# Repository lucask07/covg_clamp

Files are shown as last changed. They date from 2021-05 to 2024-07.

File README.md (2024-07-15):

# COVG Clamp Board 



Schematic and layout for the COVG bath and guard clamps. This board sits near electrodes and includes a force output and a high-impedance feedback input to create a closed-loop clamp. Intention is to use the same design for the bath and guard clamps of a COVG amplifiers. The board supports digital programming of the current measurement gain and the feedback loop stability. Switching on the board allows for connect and disconnect of electrodes and injection (or measurements) of calibration signals onto an electrode.

### The PDF plot of the board schematic is [here](docs/bath_clamp.pdf) 
- 2D capture of the 3D model of the clamp board layout: 
<p align="center">
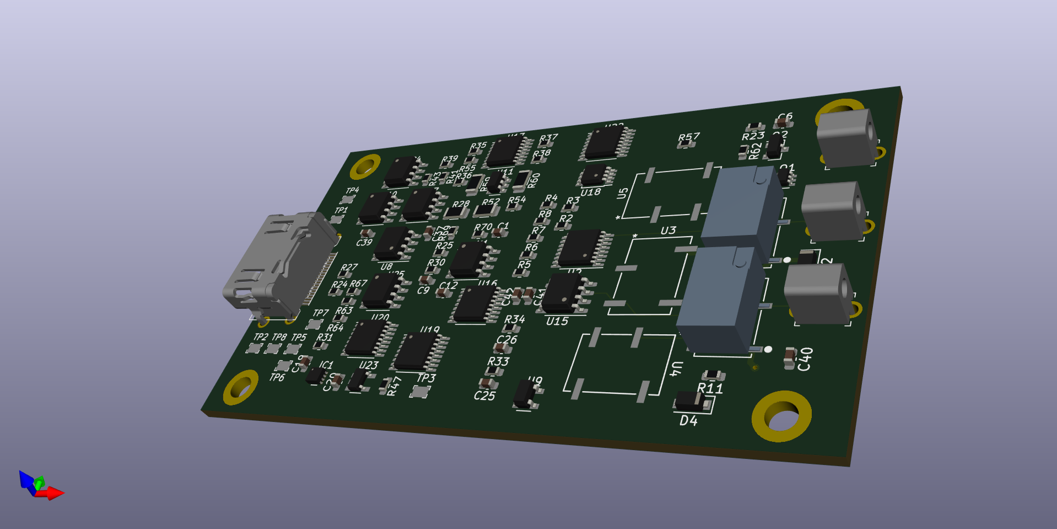
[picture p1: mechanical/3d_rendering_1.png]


## Acknowledgements 

If this work contributes to your research please cite:

I. Delgadillo Bonequi, A. Stroschein, and L. J. Koerner, “A field-programmable gate array (FPGA)-based data acquisition system for closed-loop experiments,” Review of Scientific Instruments, vol. 93, no. 11, p. 114712, Nov. 2022, [doi: 10.1063/5.0121898](http://doi.org/10.1063/5.0121898).

## HDMI: connection from DAQ to daughtercard 

The digital COVG project uses the concept of one main data acquition board connected to an FPGA. The main data acquisition board has multiple channels that extend to daughtercards. The connection to each daughtercard allows for low-latency control by connections to high-speed ADCs and DACs on the daq board. For COVG the daughtercards are the bath clamp; the guard clamp; the voltage clamp and I force; and the V1/V2. The connectivity to the daughtercard is generalized and will be the same for each. 

An HDMI-A cable is used for input and output signals that connects the bath clamp daughtercard to the DAQ board. The HDMI cable carries:

- **power**: +5V, +15V, -15V
- **GND** 
- **Analog outputs** (to ADCs): 
	- OUT\_P, OUT\_N differential pair (x1) to 5 MSPS ADC 
	- single-ended out AMP\_OUT, CAL\_ADC both to individual channel of 1 MSPS ADC (ADS8686) 
- **Analog reference**: VCM: buffered ADC common-mode voltage (nominal 2.5 V)
- **Digital inputs** (from DACs): 
	- CMD: (command signal) from 1 us settling time DAC (attenuated by x10 at board)
	- CC: (capacitive compensation) from 1 us settling time DAC. AC coupled. 
	- CAL_DAC: from 5 us settling time DAC (DAC8050). Either voltage source or current source (Howland current pump), programmable on DAQ board
- **Digital control** (I2C): SDA, SCL (@ 3.3 V levels). Pull-ups are on DAQ board not on the daughtercards! The daughtercards use a TCA9555 I/O expander to generate many control signals from the I2C interface. 
- **Utiility** grab-bag connected to test-point. Jumper on DAQ board to set to analog in, analog out or digital I/O.

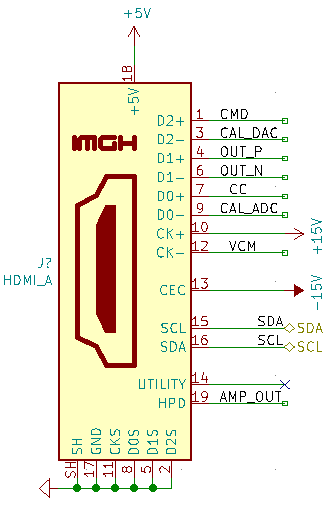
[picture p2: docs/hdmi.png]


| Pin | HDMI name    | Generic Daughtercard     | Bath clamp | Notes  |
|-----|--------------|--------------|------------|---------------------------------------------------------------------------|
| 1   | Data2+       | fastDAC1     | CMD        | ~1 us settling time                      |
| 2   | Data2 shield | Gnd          | Gnd        |                                                                           |
| 3   | Data2-       | Analog/GPIO1 | CAL_DAC    | Analog input signal from DAC8050, 16 bit, 5us settle, 5 V supply                                                                         |
| 4   | Data1+       | fastADC+     | IM_P       | to AD7960/AD7961. Differential low-pass filter on DAQ board                                                                          |
| 5   | Data1 shield | Gnd          | Gnd        |                                                                           |
| 6   | Data1-       | fastADC-     | IM_N       | to AD7960/AD7961. Differential low-pass filter on DAQ board                                                                          |
| 7   | Data0+       | fastDAC2     | CC         | ~1 us settling time                                                                          |
| 8   | Data0 shield | Gnd          | Gnd        |                                                                           |
| 9   | Data0-       | Analog/GPIO2 | CAL_ADC    | to ADS8686 1 MSPS, programmable PGA for range up to +/-10V                                                           |
| 10  | Clock+       | 15V          | 15V        | From a linear regulator on the DAQ board, 75 mA max per channel                                                                         |
| 11  | Clock shield | Gnd          | Gnd        |                                                                           |
| 12  | Clock-       | VCM          | VCM        | buffered on DAQ board, nominal 2.5 V                                                                          |
| 13  | CEC          | -15V         | -15V       | From a linear regulator on the DAQ board, 75 mA max per channel                             |
| 14  | Reserved     | open         | open       | Resistor jumper on DAQ board sets as analog in, analog out, or digital I/O (@ 3.3 V levels). Default stuffing option is to connect to the general purpose ADC (ADS8686). |
| 15  | SCL          | SCL          | SCL        | I2C clock. Pull-up on main DAQ board, 3.3 V levels                |
| 16  | SDA          | SDA          | SDA        | I2C data. Pull-up on main DAQ board, 3.3 V levels                 |
| 17  | Gnd          | Gnd          | Gnd        |                                                                           |
| 18  | 5V           | 5V           | 5V         | Power input from linear regulator, 200 mA max per channel (target)  |
| 19  | HPD          | Analog/GPIO3 | AMP_OUT    | output to ADS8686 1 MSPS, programmable PGA                        |

## Electrode Configurations and Modes 

### Electrodes

The electrode connections are [tip jack miniature PCB mount connectors](https://www.digikey.com/en/products/detail/cinch-connectivity-solutions-johnson/105-1103-001/241122?s=N4IgTCBcDaIIwAYCsBaOiDMKELiAugL5A) for 0.08" diameter pin connections. 

- J1 corresponds to Dagan P2 - force
- J2 corresponds to Dagan P1 - sense
- J3 corresponds to Dagan CC - capacitive compensation 

### Modes 
**Electrode diagnositcs / calibration / system ID** 

Five relays are used to:

1. Disconnect the electrodes from the active electronics (relay K2, K1). Digital control signals: *P1\_E\_CTRL*, *P2\_E\_CTRL*
2. Switch between active and passive clamp (U3). Digital control signals: *P\_CLAMP\_CTRL*
3. Connect calibration signals (ADC or DAC) to the electrodes (U4, U5). Digital control signals: *P1\_CAL\_CTRL*, *P2\_CAL\_CTRL*
A logical high digital control signal closes the Ux relays. A logical high swicthes the Kx relays so that the electronics and electrodes are disconnected. 

**Calibration** 
When "calibrating" the electrode that is driven by a DAC signal or output along the ADC signal CAL\_ADC is programmable. This output multiplexing is set by DAC\_SEL[1..4] and ADC\_SEL[1..4]. Via DAC\_SEL[1..4] an electrode can be connected to CAL\_DAC or GND. The ADC\_SEL[1..4] controls the signal that is connected to CAL\_ADC pin the options are (CAL\_SIG1, CAL\_SIG2, INAMP\_OUT, CC).   

**Clamping**

- _Voltage clamp_: U1 drives the command voltage (CMD) to electrode P2. Nominal voltage clamp mode will have all 5 relays in nominal position (with 0 coil current).  When in voltage clamp mode the current to P2 (as measured by the voltage across nets RF\_1 and P2) is output by the different ADC driver for 5 MSPS digitization. The settings for U22 (TMUX6136) are S1 = 1 for  the inamp output to be buffered out to the 5 MSPS ADC; and S2 = 1 so that the instrumentation amplifier amplifies the voltage difference: (P2 - RF_1). The voltage feedback in voltage clamp mode can be enabled/disabled by the I/O expander siganl *FDBK* (*FDBK*=0 is disabled). 

- _Current clamp_: The board has a Howland current source that can be used to set the current to P2 based upon the CMD signal (requires A2=A1=A0=0). The output current can range from +/-0.26 nA (with a 1.22 mV CMD) to +/-2.1 uA (with a 10 V CMD signal). To enable the current clamp either float or drive high the signal EN\_IPUMP. To shutoff the amplifier set EN\_IPUMP to a logical 0. When in current clamp mode the intent is that the 5 MSPS ADC measurement is of P1 (i.e. set current and measure voltage). This is accomplished by these settings for U22 (TMUX6136): S1 = 0 so that the P2 buffer output voltage is sent to the 5 MSPS ADC; and S2 = 0 so that the instrumentation amplifier amplifies P2 - 0 (RF_1 voltage will not make sense in this mode). In this mode the instrumentation amplifier output can buffer out the CAL\_OUT line to a 1 MSPS ADC channel. 

### Adjustments for clamp stability 
The P2 signal is amplified and buffered before being fedback to the main clamp amplifier (U15 within feedback\_buffer). The stability of this loop varies depending upon the load presented by the cell under test, electrode electrical characteristics, and parasitic capacitive coupling between electrodes. The stability of this feedback loop can be adjusted by modification of the feedback buffer gain and by changing the capacitance of a lead compensator at the summing junction of the main amplifier (inverting terminal). 

**Feedback buffer gain**

The feedback buffer is a non-inverting structure with an adjustable gain set by I/O expander bits RF[1..4]. The feedback resistor values are 3.01k, 12.1k, 30.1k, and 60.4k. The resistor from the inverting terminal to "ground" is 3.01k creating gains of 

- x2 = 1+3.01k/3.01k 
- x5 
- x11
- x21 

**Feedback buffer offset**

The feedback buffer has offset adjustment. This is generated by a 10-bit I2C interface DAC, IC1 (DAC53401), followed by a unipolar to bipolar amplifier (U23). The output of the bipolar converter ranges between +/-1 V (resolution of 1.9 mV / bit). OUT = VDAC*1.666-1. 

(simulation: non\_inverting\_rpot\_bw.asc)

**Compensation adjustment**

Adjustments of the closed-loop stability are achieved using four approaches. 

- The primary approach is a lead compensator formed by R30 in parallel with the capacitors in the compensation switching sheet. This method is presented in "Voltage Clamping of Excitable Membranes" by Bezanilla, Vergara, and Taylor. The compensation capacitors (47 pF, 200 pF, 1 nF, 4.7 nF) are selectable using the the TMUX6111 I/O expander bits CCOMP[1..4].
- A second approach is adjusting the gain of the feedback buffer (see above). 
- A third approach is a stabilizing feedback network of R in series with C; simulations have shown little beneift of this network. Also, beware that the C forms a pole with the current resolving resistor (R\_F) which can be very low frequency. The footprints for these components are included by not populated. This is also presented in Bezanilla, et al.
- The fourth potential approach is an input lead-lag compensator formed by R69 and C37 (unpopulated). See [TI App Note AN-1604](https://www.ti.com/lit/an/snoa486b/snoa486b.pdf?ts=1623954308102&ref_url=https%253A%252F%252Fwww.google.com%252F)

### Adjustments for current measurement

The current measurement gain (historically reported in units of mV/nA) is determined by three separate "stages".

**Resolving inline resistor**: is set by component U2 which is an analog switch (ADG1208) that determines the resistance across which the clamp current is measured. 

| Ref. Des. | Value    | mV/nA            | A2,A1,A0 | Closed Switch   | 
|-----|--------------|--------------|------------|------------|
| none -> Iclamp| n/a | n/a | 0,0,0 | Sw1 |
| R2   | 10 kOhm       |  0.01       | 0,0,1 | Sw2      | 
| R3   | 33.2 kOhm       |  0.033       | 0,1,0 | Sw3      | 
| R4   | 100k Ohm       |  0.1       | 0,1,1 | Sw4      | 
| R5   | 332 kOhm       |  0.332       | 1,0,0 | Sw4      | 
| R6   | 1 MOhm       |  1       | 1,0,1 | Sw5      | 
| R7   | 3.32 MOhm       |  3.32       | 1,1,0 | Sw6      | 
| R8   | 10 MOhm       |  10       | 1,1,1 | Sw7      | 

**Instrumentation Amplifier gain**  

There is a second stage that allows for additional gain on the analog output signal before ADC conversion. The gain of the instrumentation amplifier (AD8421) within the adc\_driver block gain is adjusted with bits G[1..3].
The gain options as controled by U17 (DG412 switch) are: 

- G = 1, G1=G2=G3=0, all switches open 
- G = 1.99, G1 = 1, others = 0 
- G = 4.98, G2 = 1, others = 0
- G = 10.00, G3 = 1, others = 0 
- G = 50, This setting is currently not programmable but set by resistors. 
- Other gains are available by combining the gain settings resistors in parallel. 

For the instrumentation amplifier Gain = 1 + 9.9 kOhm/RG 

**Output ADC driver gain**

The ADC output driver implements a gain of around 1/3 (0.308 = 499 Ohms/(1500 + 120) Ohms) to scale the maximum output of the instrumenation amplifer (+/-13.5 V) to the range of the AD796x ADC (+/-4.096 V).

**Total gain** 

(without the G = 50 option of the instrumentation amplifier) the available gain ranges are:

- min: 0.00308 mV/nA 
- max: 30.8 mV/nA. 

Since the ADC covers a range of +/-4.096 V at 16-bit resolution for step-sizes of:

- min-gain: 0.0246 LSB/nA  (40.6 nA/LSB)
- max-gain: 246.4 LSB/nA  (4.06 pA/LSB)

The amplifier noise simulates to be (very roughly) 1 nA RMS, such that ADC quantization noise will not limit amplifier performance when high-gain settings are used.

## I2C Address Table
| Component | Description | I2C address | I2C mode | 
| --------- | -------- | ------------| ------------|
| U12    | I/O expander 0: TCA9555       | 0x26 = 'b010\_0110 | Standard, Fast |
| U13    | I/O expander 1: TCA9555        | 0x20 = 'b010\_0000 | Standard, Fast |
| U6   | Unique ID EEPROM: 24AA025UID    | 0x50 = 'b101\_0000 | Standard, Fast |
| IC1   | Offset adj. DAC: DAC53401  | 0x48 = 'b100\_1000 | Standard, Fast, Fast+ |

## Current Draw

+/-15 V  (or from the +7V and -2.5 V supplies derived from +/-15 V) 

| Component | Quantity | Current [mA]| Total [mA] |
| --------- | -------- | ------------| ---------- |
| OPA828    | 2        | 5.5 | 11 |
| OPA2156   | 2 (dual) | 4.4 | 8.8 |
| OPA991S   | 1        | 0.56 | 0.56 |
| ADG1208   | 1        | 0.0001 | 0 |
| ADG1208   | 1        | 0.0001 | 0 |
| AD8421    | 1        | 2.3    | 2.3 |
| ADA4932 (ADC driver)  | 1        | 9.6    |     |
| or LMP8350 (ADC driver) |         | 15 (HP mode) | 15 |
|           |          |        | Totals (w/ LMP) |
|           |          |        |    37.66 |

## For Board and FPGA Designers

## KiCAD Setup (libraries)
Before opening the project complete these steps to setup your parts libraries. 

* On the main Kicad Menu bar click 'Preferences' -> 'Configure Paths'. 
* Then within the 'Configure Paths' window create an Environmental Variable with the 'Name' MYLIBRARY.
* Set the 'Path' to be where you will store the Digikey libraries and the COVG custom library. For example (this is on a MAC) '/Users/lucas/Documents/kicad/libraries'.

Now *git clone* (effectively download) the digikey and COVG libraries. 

* The Digikey library is at [https://github.com/Digi-Key/digikey-kicad-library](https://github.com/Digi-Key/digikey-kicad-library)
	* Use the terminal command: `git clone https://github.com/Digi-Key/digikey-kicad-library.git ` 

* The custom COVG library is at [https://github.com/lucask07/covg-kicad-lib](https://github.com/lucask07/covg-kicad-lib)
	* Use the terminal command: `git clone https://github.com/lucask07/covg-kicad-lib.git `
	* This is a private repository so will require you to request access to the repository from Lucas. 

Symbols and footprints custom to this design (and the COVG project in general) are housed in the [covg-kicad-lib repository](https://github.com/lucask07/covg-kicad-lib). This library should be a project specific library in your KiCAD *Symbol Library Management* and *Footprint Library Management*. 

* Another library in use is the [agg library](https://github.com/adamgreig/agg-kicad)

### LMP8350 ADC Driver 

Initial designs used the ADA4932-1 differential ADC driver to drive the AD7961 on the DAQ board. However, as part of the "chip shortage of 2021" there parts were hard to find in spring of 2021. An alternative part (and possibly better option) used for this board is the [LMP8350](https://rocelec.widen.net/view/pdf/d6pm6sbaz5/lmp8350.pdf?t.download=true&u=5oefqw).

## BOM (bill of materials)

The BOM is available [here](bom/bath_clamp_v1_bom.xlsx)

Two command-line tools are useful for finding and ordering the parts for the board. 

[kifield](https://xess.com/KiField/docs/_build/singlehtml/index.html): extracts all fields from components on the schematic into a spreadsheet and also allows for "injecting" updates in the spreadsheet into the schematic.

Example to extract parts:
```kifield -x covg_daq_v2.sch --recurse -i covg_daq_v2_parts.csv```

**Don't import parts from the CSV into the board! This seems to incorrectly update some components!!**:
``` kifield -x covg_daq_v2_parts.csv --recurse -i covg_daq_v2.sch ```

[kicost](https://github.com/xesscorp/KiCost) which scrapes availability and prices from various distributors and creates a spreadsheet of component cost. 

## Changelog (v1 ---> v2)
List on NB#1 pg 76.

1. Add an 'Alternate Manf#' field to all ICs (where possible). The alternative part must be pin compatible. If available add an 'Alternate2 Manf#'. If the alternative part requires a footprint change the field is 'Alternate Manf# (footprint diff)'.
2. Use +/-15 V op-amp to buffer 3.3 V into amplifier. Eliminates problem of the 3.3 V net rising since the regulator cannot sink current. 
3. Switch to a DAC with leads to improve solderability. Part chosen was the DAC101C081CIMK/NOPB.
4. Correct ADG1208 Manf# to ADG1208YRUZ so that the package matches the footprint (16-TSSOP).  
5. Switch LM337 negative regulator to MIC5270YM5-TR (alternate MIC5270-4.1YM5-TR, fixed -4.1 V).  Another option considered was the TPS7A3401DGNT. 
6. Change resistor values in adjustable regulators for lower negative voltage. The negative regulator is designed for either an adjustable version or a fixed voltage. The resistor values are 487 Ohm and 240 Ohm for -3.635 Volts. 
7. Need alternative to the AD8421 instrumentation amplifier in 8-MSOP. Locating an 8-MSOP instrumentation amplifier was challenging. Switched to an 8-SOIC footprint. 
8. The SMT SPDT relay 1462042-8 was not avaliable. The through hole version is available 1462042-7. Added new footprint to covg-library named Relay_SPDT_TE_1462042-7.
9. Need alternative to the TMUX6136 (or switch to a 4x SPST + 2 channel inverter). The findchips risk for the TMUX6136 was low so kept this part but added 0 Ohm resistors that can be populated for a default MUX configuration.
10. Mini banana  NOT YET DONE!
11. More ground test points  NOT YET DONE!
12. Fixed swap of SCL and SDA (correct by changing routing at the connector to keep other routing correct) NOT YET DONE!
13. The TCA9555DBR (IO expander) has another Manf# for the same part as TCA9555DBT. The PCA9555 is an older part that is also compatible with the TCA9555. 
14. The microchip 3.3 V regulator is not available (MCP1804T-3302I/OT). 

Use the Value field to indiciate DNI (do not install) but keep the MANF# up to date. 

## Funding 
Research reported in this publication was supported by the National Institute Of Neurological Disorders And Stroke of the National Institutes of Health under Award Number R15NS116907. The content is solely the responsibility of the authors and does not necessarily represent the official views of the National Institutes of Health.

<!---
## Block diagram - To Be Completed! 
drawio (also named add.diagrams.net) is used to create block diagrams by integrating drawio with the GitHub repository. 

![Test block diagram](docs/test_github.svg)

--->

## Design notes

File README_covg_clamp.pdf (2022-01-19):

Schematic and layout for the COVG bath and guard clamps. This board sets near electrodes and includes a force output and a high-impedance feedback input to create a closed-loop clamp. Intention is to use the same design for the bath and guard clamps of a COVG amplifiers. The board supports digital programming of the current measurement gain and the feedback loop stability. Switching on the board allows for connect and disconnect of electrodes and injection (or measurements) of calibration signals onto an electrode.

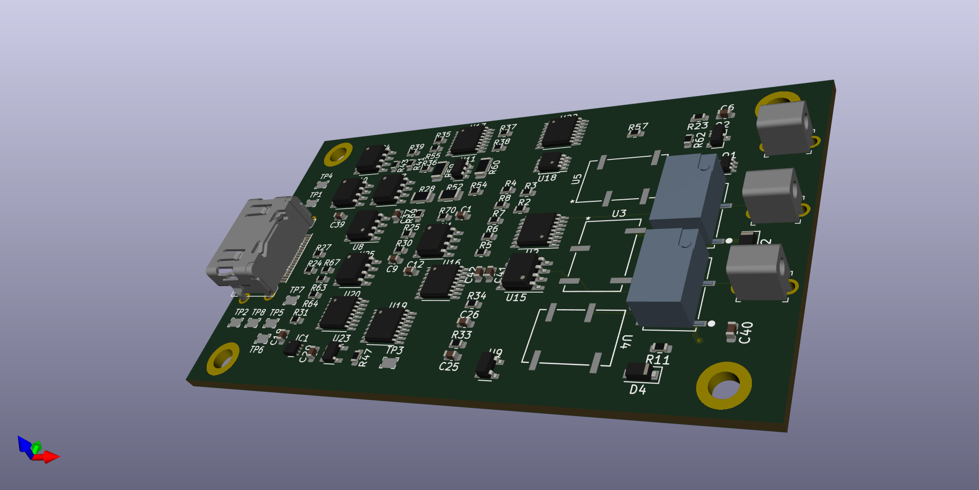
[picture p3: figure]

2D capture of the 3D model of the clamp board layout:

The digital COVG project uses the concept of one main data acquition board connected to an FPGA. The main data acquisition board has multiple channels that extend to daughtercards. The connection to each daughtercard allows for low-latency control by connections to high-speed ADCs and DACs on the daq board. For COVG the daughtercards are the bath clamp; the guard clamp; the voltage clamp and I force; and the V1/V2. The connectivity to the daughtercard is generalized and will be the same for each.

An HDMI-A cable is used for input and output signals that connects the bath clamp daughtercard to the DAQ board. The HDMI cable carries:

power: +5V, +15V, -15V
GND
Analog outputs (to ADCs):

OUT_P, OUT_N differential pair (x1) to 5 MSPS ADC

# COVG Clamp Board

## The PDF plot of the board schematic is here

# HDMI: connection from DAQ to daughtercard

single-ended out AMP_OUT, CAL_ADC both to individual channel of 1 MSPS ADC (ADS8686)

Analog reference: VCM: buffered ADC common-mode voltage (nominal 2.5 V)
Digital inputs (from DACs):

CMD: (command signal) from 1 us settling time DAC (attenuated by x10 at board)
CC: (capacitive compensation) from 1 us settling time DAC. AC coupled.
CAL_DAC: from 5 us settling time DAC (DAC8050). Either voltage source or current source (Howland current pump), programmable on DAQ board

Digital control (I2C): SDA, SCL (@ 3.3 V levels). Pull-ups are on DAQ board not on the daughtercards! The daughtercards use a TCA9555 I/O expander to generate many control signals from the I2C interface. Utiility grab-bag connected to test-point. Jumper on DAQ board to set to analog in, analog out or digital I/O.

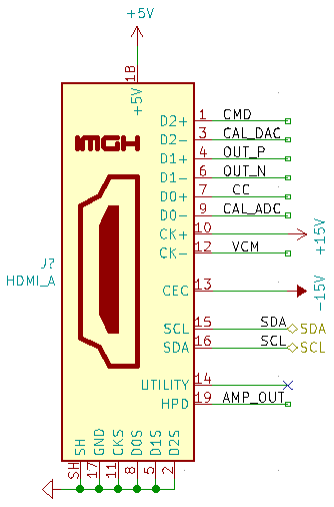
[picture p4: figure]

Pin | HDMI | Generic | Bath | Notes

| name | Daughtercard | clamp
1 | Data2+ | fastDAC1 | CMD | ~1 us settling time
2 | Data2 shield | Gnd | Gnd
3 | Data2- | Analog/GPIO1 | CAL_DAC | Analog input signal from DAC8050, 16 bit, 5us settle, 5 V supply
4 | Data1+ | fastADC+ | IM_P | to AD7960/AD7961. Differential low-pass filter on DAQ board
5 | Data1 shield | Gnd | Gnd
6 | Data1- | fastADC- | IM_N | to AD7960/AD7961. Differential low-pass filter on DAQ board
7 | Data0+ | fastDAC2 | CC | ~1 us settling time
8 | Data0 shield | Gnd | Gnd
9 | Data0- | Analog/GPIO2 | CAL_ADC | to ADS8686 1 MSPS, programmable PGA for range up to +/-10V
10 | Clock+ | 15V | 15V | From a linear regulator on the DAQ board, 75 mA max per channel
11 | Clock shield | Gnd | Gnd
12 | Clock- | VCM | VCM | buffered on DAQ board, nominal 2.5 V
13 | CEC | -15V | -15V | From a linear regulator on the DAQ board, 75 mA max per channel
14 | Reserved | open | open | Resistor jumper on DAQ board sets as analog in, analog out, or digital I/O (@ 3.3 V levels). Default stuffing option is to connect to the general purpose ADC (ADS8686).
15 | SCL | SCL | SCL | I2C clock. Pull-up on main DAQ board, 3.3 V levels

16 | SDA | SDA | SDA | I2C data. Pull-up on main DAQ board, 3.3 V levels
17 | Gnd | Gnd | Gnd
18 | 5V | 5V | 5V | Power input from linear regulator, 200 mA max per channel (target)
19 | HPD | Analog/GPIO3 | AMP_OUT | output to ADS8686 1 MSPS, programmable PGA

The electrode connections are tip jack miniature PCB mount connectors (https://www.digikey.com/en/products/detail/cinch-connectivity-solutions-johnson/105-1103-001/241122?s=N4IgTCBcDaIIwAYCsBaOiDMKELiAugL5A) for 0.08" diameter pin connections.

J1 corresponds to Dagan P2 - force
J2 corresponds to Dagan P1 - sense
J3 corresponds to Dagan CC - capacitive compensation

Electrode diagnositcs / calibration / system ID

Five relays are used to:

1. Disconnect the electrodes from the active electronics (relay K2, K1). Digital control signals: P1_E_CTRL, P2_E_CTRL
2. Switch between active and passive clamp (U3). Digital control signals: P_CLAMP_CTRL
3. Connect calibration signals (ADC or DAC) to the electrodes (U4, U5). Digital control signals: P1_CAL_CTRL, P2_CAL_CTRL A logical high digital control signal closes the Ux relays. A logical high swicthes the Kx relays so that the electronics and electrodes are disconnected.

Calibration When "calibrating" the electrode that is driven by a DAC signal or output along the ADC signal CAL_ADC is programmable. This output multiplexing is set by DAC_SEL[1..4] and ADC_SEL[1..4]. Via DAC_SEL[1..4] an electrode can be connected to CAL_DAC or GND. The ADC_SEL[1..4] controls the signal that is connected to CAL_ADC pin the options are (CAL_SIG1, CAL_SIG2, INAMP_OUT, CC).

Clamping

Voltage clamp: U1 drives the command voltage (CMD) to electrode P2. Nominal voltage clamp mode will have all 5 relays in nominal position (with 0 coil current). When in voltage clamp mode the current to P2

# Electrode Configurations and Modes

## Electrodes

## Modes

(as measured by the voltage across nets RF_1 and P2) is output by the different ADC driver for 5 MSPS digitization. The settings for U22 (TMUX6136) are S1 = 1 for the inamp output to be buffered out to the 5 MSPS ADC; and S2 = 1 so that the instrumentation amplifier amplifies the voltage difference: (P2 - RF_1). The voltage feedback in voltage clamp mode can be enabled/disabled by the I/O expander siganl FDBK (FDBK=0 is disabled).

Current clamp: The board has a Howland current source that can be used to set the current to P2 based upon the CMD signal (requires A2=A1=A0=0). The output current can range from +/-0.26 nA (with a 1.22 mV CMD) to +/-2.1 uA (with a 10 V CMD signal). To enable the current clamp either float or drive high the signal EN_IPUMP. To shutoff the amplifier set EN_IPUMP to a logical 0. When in current clamp mode the intent is that the 5 MSPS ADC measurement is of P1 (i.e. set current and measure voltage). This is accomplished by these settings for U22 (TMUX6136): S1 = 0 so that the P2 buffer output voltage is sent to the 5 MSPS ADC; and S2 = 0 so that the instrumentation amplifier amplifies P2 - 0 (RF_1 voltage will not make sense in this mode). In this mode the instrumentation amplifier output can buffer out the CAL_OUT line to a 1 MSPS ADC channel.

The P2 signal is amplified and buffered before being fedback to the main clamp amplifier (U15 within feedback_buffer). The stability of this loop varies depending upon the load presented by the cell under test, electrode electrical characteristics, and parasitic capacitive coupling between electrodes. The stability of this feedback loop can be adjusted by modification of the feedback buffer gain and by changing the capacitance of a lead compensator at the summing junction of the main amplifier (inverting terminal).

Feedback buffer gain

The feedback buffer is a non-inverting structure with an adjustable gain set by I/O expander bits RF[1..4]. The feedback resistor values are 3.01k, 12.1k, 30.1k, and 60.4k. The resistor from the inverting terminal to "ground" is 3.01k creating gains of

x2 = 1+3.01k/3.01k
x5
x11
x21

Feedback buffer offset

The feedback buffer has offset adjustment. This is generated by a 10-bit I2C interface DAC, IC1 (DAC53401), followed by a unipolar to bipolar amplifier (U23). The output of the bipolar converter ranges between +/-1 V (resolution of 1.9 mV / bit). OUT = VDAC*1.666-1.

## Adjustments for clamp stability

(simulation: non_inverting_rpot_bw.asc)

Compensation adjustment

Adjustments of the closed-loop stability are achieved using four approaches.

The primary approach is a lead compensator formed by R30 in parallel with the capacitors in the compensation switching sheet. This method is presented in "Voltage Clamping of Excitable Membranes" by Bezanilla, Vergara, and Taylor. The compensation capacitors (47 pF, 200 pF, 1 nF, 4.7 nF) are selectable using the the TMUX6111 I/O expander bits CCOMP[1..4].
A second approach is adjusting the gain of the feedback buffer (see above).
A third approach is a stabilizing feedback network of R in series with C; simulations have shown little beneift of this network. Also, beware that the C forms a pole with the current resolving resistor (R_F) which can be very low frequency. The footprints for these components are included by not populated. This is also presented in Bezanilla, et al.
The fourth potential approach is an input lead-lag compensator formed by R69 and C37 (unpopulated). See TI App Note AN-1604 (https://www.ti.com/lit/an/snoa486b/snoa486b.pdf?ts=1623954308102)

The current measurement gain (historically reported in units of mV/nA) is determined by three separate "stages".

Resolving inline resistor: is set by component U2 which is an analog switch (ADG1208) that determines the resistance across which the clamp current is measured.

Ref. Des. | Value | mV/nA | A2,A1,A0 | Closed Switch
none -> Iclamp | n/a | n/a | 0,0,0 | Sw1
R2 | 10 kOhm | 0.01 | 0,0,1 | Sw2
R3 | 33.2 kOhm | 0.033 | 0,1,0 | Sw3
R4 | 100k Ohm | 0.1 | 0,1,1 | Sw4
R5 | 332 kOhm | 0.332 | 1,0,0 | Sw4
R6 | 1 MOhm | 1 | 1,0,1 | Sw5
R7 | 3.32 MOhm | 3.32 | 1,1,0 | Sw6
R8 | 10 MOhm | 10 | 1,1,1 | Sw7

## Adjustments for current measurement

Instrumentation Amplifier gain

There is a second stage that allows for additional gain on the analog output signal before ADC conversion. The gain of the instrumentation amplifier (AD8421) within the adc_driver block gain is adjusted with bits G[1..3]. The gain options as controled by U17 (DG412 switch) are:

G = 1, G1=G2=G3=0, all switches open
G = 1.99, G1 = 1, others = 0
G = 4.98, G2 = 1, others = 0
G = 10.00, G3 = 1, others = 0
G = 50, This setting is currently not programmable but set by resistors. Other gains are available by combining the gain settings resistors in parallel.

For the instrumentation amplifier Gain = 1 + 9.9 kOhm/RG

Output ADC driver gain

The ADC output driver implements a gain of around 1/3 (0.308 = 499 Ohms/(1500 + 120) Ohms) to scale the maximum output of the instrumenation amplifer (+/-13.5 V) to the range of the AD796x ADC (+/-4.096 V).

Total gain

(without the G = 50 option of the instrumentation amplifier) the available gain ranges are:

min: 0.00308 mV/nA
max: 30.8 mV/nA.

Since the ADC covers a range of +/-4.096 V at 16-bit resolution for step-sizes of:

min-gain: 0.0246 LSB/nA (40.6 nA/LSB)
max-gain: 246.4 LSB/nA (4.06 pA/LSB)

The amplifier noise simulates to be (very roughly) 1 nA RMS, such that ADC quantization noise will not limit amplifier performance when high-gain settings are used.

# I2C Address Table

Component | Description | I2C address | I2C mode
U12 | I/O expander 0: TCA9555 | 0x26 = 'b010_0110 | Standard, Fast
U13 | I/O expander 1: TCA9555 | 0x20 = 'b010_0000 | Standard, Fast
U6 | Unique ID EEPROM: 24AA025UID | 0x50 = 'b101_0000 | Standard, Fast
IC1 | Offset adj. DAC: DAC53401 | 0x48 = 'b100_1000 | Standard, Fast, Fast+

+/-15 V (or from the +7V and -2.5 V supplies derived from +/-15 V)

Component | Quantity | Current [mA] | Total [mA]
OPA828 | 2 | 5.5 | 11
OPA2156 | 2 (dual) | 4.4 | 8.8
OPA991S | 1 | 0.56 | 0.56
ADG1208 | 1 | 0.0001 | 0
ADG1208 | 1 | 0.0001 | 0
AD8421 | 1 | 2.3 | 2.3
ADA4932 (ADC driver) | 1 | 9.6
or LMP8350 (ADC driver) | | 15 (HP mode) | 15
| | | Totals (w/ LMP)
| | | 37.66

Before opening the project complete these steps to setup your parts libraries.

On the main Kicad Menu bar click 'Preferences' -> 'Configure Paths'.

# Current Draw

# For Board and FPGA Designers

# KiCAD Setup (libraries)

Then within the 'Configure Paths' window create an Environmental Variable with the 'Name' MYLIBRARY. Set the 'Path' to be where you will store the Digikey libraries and the COVG custom library. For example (this is on a MAC) '/Users/lucas/Documents/kicad/libraries'.

Now git clone (effectively download) the digikey and COVG libraries.

The Digikey library is at https://github.com/Digi-Key/digikey-kicad-library

The custom COVG library is at https://github.com/lucask07/covg-kicad-lib

Use the terminal command:
git clone https://github.com/lucask07/covg-kicad-lib.git
This is a private repository so will require you to request access to the repository from Lucas.

Symbols and footprints custom to this design (and the COVG project in general) are housed in the covg-kicad-lib repository. This library should be a project specific library in your KiCAD Symbol Library Management and (https://github.com/lucask07/covg-kicad-lib) Footrpint Library Management.

Initial designs used the ADA4932-1 differential ADC driver to drive the AD7961 on the DAQ board. However, as part of the "chip shortage of 2021" there parts were hard to find in spring of 2021. An alternative part (and possibly better option) used for this board is the LMP8350. (https://rocelec.widen.net/view/pdf/d6pm6sbaz5/lmp8350.pdf?t.download=true&u=5oefqw)

The BOM is available here

Two command-line tools are useful for finding and ordering the parts for the board.

kifield: (https://xess.com/KiField/docs/_build/singlehtml/index.html) extracts all fields from components on the schematic into a spreadsheet and also allows for "injecting" updates in the spreadsheet into the schematic.

Example to extract parts: kifield -x covg_daq_v2.sch --recurse -i covg_daq_v2_parts.csv

Don't import parts from the CSV into the board! This seems to incorrectly update some components!!: kifield -x covg_daq_v2_parts.csv --recurse -i covg_daq_v2.sch

kicost (https://github.com/xesscorp/KiCost) which scrapes availability and prices from various distributors and creates a spreadsheet of component

## LMP8350 ADC Driver

# BOM (bill of materials)

cost.

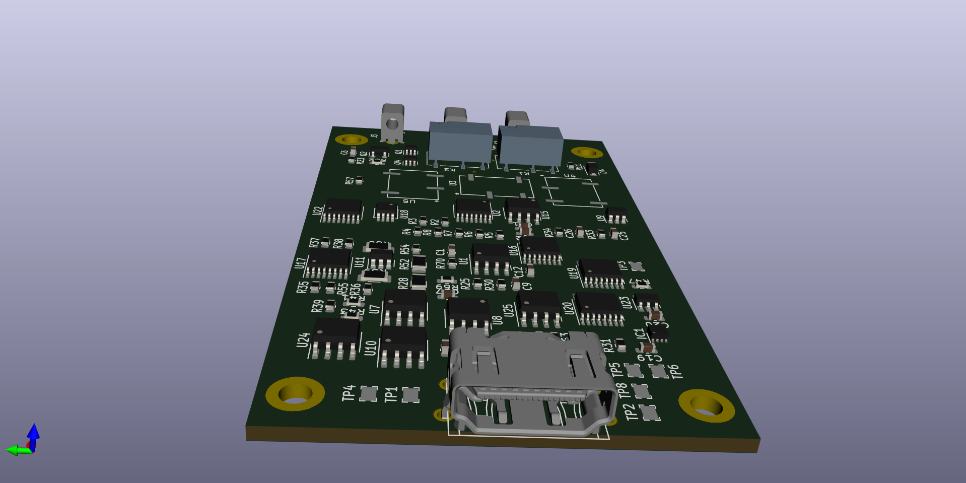
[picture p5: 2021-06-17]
mechanical/3d_rendering_2.png

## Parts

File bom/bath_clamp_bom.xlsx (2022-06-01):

Source: | /Users/koer2434/My Drive/UST/research/covg/pcb_design/kicad/covg_clamp/bath_clamp.sch
Date: | Monday, April 11, 2022 at 04:43:50 PM
Tool: | Eeschema (5.1.12-1-10_14)
Generator: | /Applications/KiCad/kicad.app/Contents/SharedSupport/plugins/bom_csv_grouped_by_value.py
Component Count: | 170
Individual Components:
Item | Qty | Reference(s) | Value | Tolerance | voltage | Manf# | Alternate Manf# | Alternate2 Manf# | Alternate3 Manf# | Alternate4 Manf# | Alternate Manf# (footprint diff)
 |  | C1 | DNI
 |  | C2 | 1u | 10% | 25V | 06033C105KAT4A
 |  | C3 | 10u | 10% | 16V | CL21A106KOQNNNE
 |  | C4 | 0.1u | 10% | 25V | CL10B104KA8NNWC
 |  | C5 | 4.7u | 20% | 25V | CL10A475KP8NNNC
 |  | C6 | 4.7n | 5% | 50V | CC0603JRX7R9BB472
 |  | C7 | 0.1u | 20% | 25V | CC0603MRX7R8BB104
 |  | C8 | 0.1u | 20% | 25V | CC0603MRX7R8BB104
 |  | C9 | 47pF | 5% | 50V | CC0603JRNPO9BN470
 |  | C10 | 200pF |  | 50V | CC0603JRNPO9BN221
 |  | C11 | 1nF | 5% | 50V | CC0603JRNPO9BN102
 |  | C12 | 4.7nF | 5% | 50V | CC0603JRNPO9BN332 | CL10C332JB8NNNC
 |  | C13 | 0.1u | 20% | 25V | CC0603MRX7R8BB104
 |  | C14 | 0.1u |  | 25V | CC0603MRX7R8BB104
 |  | C15 | 4.7u | 10% | 25V | CL31B475KAHNFNE
 |  | C16 | 4.7u | 10% | 25V | CL31B475KAHNFNE
 |  | C17 | 0.01u | 20% | 25V | CC0603MRX7R8BB103
 |  | C18 | 0.01u | 20% | 25V | CC0603MRX7R8BB103
 |  | C19 | 0.01u | 20% | 25V | CC0603MRX7R8BB103
 |  | C20 | 0.1u | 20% | 25V | CC0603MRX7R8BB104
 |  | C21 | 0.1u | 20% | 25V | CC0603MRX7R8BB104
 |  | C22 | 0.1u | 20% | 25V | CC0603MRX7R8BB104
 |  | C23 | 68p | 20% | 25V | CC0603FRNPO0BN680
 |  | C24 | 20p | 20% | 25V | CC0603JRNPO9BN200
 |  | C25 | 8p | 20% | 25V | 06031A8R0CAT2A
 |  | C26 | 4p | 20% | 25V | CC0603CRNPO9BN4R0
 |  | C27 | DNI |  |  | CC0603FRNPO0BN680
 |  | C28 | DNI |  |  | CC0603FRNPO0BN680
 |  | C29 | 0.1u | 20% | 25V | CC0603MRX7R8BB104
 |  | C30 | 0.1u |  | 25V | CC0603MRX7R8BB104
 |  | C31 | 0.1u | 20% | 25V | CC0603MRX7R8BB104
 |  | C32 | 0.1u |  | 25V | CC0603MRX7R8BB104
 |  | C33 | 5p | 5% | 50V | CC0603JRX7R9BB472
 |  | C34 | 0.1u | 20% | 25V | CC0603MRX7R8BB104
 |  | C35 | 0.1u |  | 25V | CC0603MRX7R8BB104
 |  | C36 | 0.1u | 20% | 25V | CC0603MRX7R8BB104
 |  | C37 | DNI | 20% | 25V | CC0603MRX7R8BB104
 |  | C38 | 0.1u |  | 25V | CC0603MRX7R8BB104
 |  | C39 | 0.1u | 20% | 25V | CC0603MRX7R8BB104
 |  | C40 | 0.1u |  | 25V | CC0603MRX7R8BB104
 |  | C41 | 0.1u | 20% | 25V | CC0603MRX7R8BB104
 |  | C42 | 0.1u | 20% | 25V | CC0603MRX7R8BB104
 |  | C43 | 0.1u | 20% | 25V | CC0603MRX7R8BB104
 |  | C44 | 0.1u | 20% | 25V | CC0603MRX7R8BB104
 |  | C45 | 10u | 10% | 25V | CL31B106KAHNFNE
 |  | C46 | 10u | 10% | 25V | CL31B106KAHNFNE
 |  | C47 | 0.1u |  | 25V | CC0603MRX7R8BB104
 |  | C48 | DNI | 5% | 50V | CC0603JRX7R9BB472
 |  | C49 | DNI | 5% | 50V | CC0603JRNPO9BN100
 |  | D1 | 1N4007 |  |  | 1N4007FLTR
 |  | D2 | 1N4007 |  |  | 1N4007FLTR
 |  | D3 | 1N4007 |  |  | 1N4007FLTR
 |  | D4 | 1N4007 |  |  | 1N4007FLTR
 |  | D5 | 1N4007 |  |  | 1N4007FLTR
 |  | FB1 | Ferrite_Bead |  |  | BLM31PG500SN1L
 |  | H1 | DNI
 |  | H3 | DNI
 |  | H5 | DNI
 |  | H7 | DNI
 |  | IC1 | DAC101C081CIMK_NOPB |  |  | DAC101C081CIMK/NOPB | DAC121C081CIMK/NOPB
 |  | J1 | 105-1103-001 |  |  | 105-1103-001
 |  | J2 | 105-1103-001 |  |  | 105-1103-001
 |  | J3 | 105-1103-001 |  |  | 105-1103-001
 |  | J4 | HDMI_A |  |  | 10029449-111RLF
 |  | J5 | Conn_01x04 |  |  | PR20204VBNN
 |  | K1 | 1462042-7 |  |  | 1462042-7 |  |  |  |  | 1462042-8
 |  | K2 | 1462042-7 |  |  | 1462042-7 |  |  |  |  | 1462042-8
 |  | Q1 | MBT3904DW1T1G |  |  | MBT3904DW1T1G
 |  | Q2 | BC856 |  |  | BC856B-7-F
 |  | Q3 | MBT3904DW1T1G |  |  | MBT3904DW1T1G
 |  | Q4 | MBT3904DW1T1G |  |  | MBT3904DW1T1G
 |  | R1 | 0 | 5% |  | RC0603FR-070RL
 |  | R2 | 10k | 5% |  | RC0603FR-0710KL
 |  | R3 | 33.2k | 5% |  | RC0603FR-0733K2L
 |  | R4 | 100k | 5% |  | RC0603FR-07100KL
 |  | R5 | 332k | 5% |  | RC0603FR-07332KL
 |  | R6 | 1M | 5% |  | RC0603FR-071ML
 |  | R7 | 3.32M | 5% |  | RC0603FR-073M32L
 |  | R8 | 10M | 5% |  | RC0603FR-0710ML
 |  | R9 | 10k | 5% |  | RC0603FR-0710KL
 |  | R10 | 10k | 5% |  | RC0603FR-0710KL
 |  | R11 | 10k | 5% |  | RC0603FR-0710KL
 |  | R12 | 10k | 5% |  | RC0603FR-0710KL
 |  | R13 | 10k | 5% |  | RC0603FR-0710KL
 |  | R14 | 240 | 1% |  | RC0603FR-07240RL
 |  | R15 | 487 | 1% |  | RC0603FR-07487RL
 |  | R16 | 1.13k | 1% |  | RC0603FR-071K13L
 |  | R17 | 240 | 1% |  | RC0603FR-07240RL
 |  | R18 | 33 | 1% |  | RC0603FR-0733RL
 |  | R19 | 20k | 5% |  | RC0603FR-0720KL
 |  | R20 | 0 | 5% |  | RC0603FR-070RL
 |  | R21 | 2k | 1% |  | RC0603FR-0773K2L
 |  | R22 | 10k | 5% |  | RC0603FR-0710KL
 |  | R23 | 0 | 5% |  | RC0603FR-070RL
 |  | R24 | 33 | 1% |  | RC0603FR-0733RL
 |  | R25 | 20k | 1% |  | RC0603FR-0720KL
 |  | R26 | 0 | 5% |  | RC0603FR-070RL
 |  | R27 | 0 | 5% |  | RC0603FR-070RL
 |  | R28 | 4.7M | 0.1 |  | RG3216P-4704-B-T1
 |  | R29 | DNI | 1% |  | RC0603FR-0773K2L
 |  | R30 | 20k | 1% |  | RC0603FR-0720KL
 |  | R31 | 10k | 5% |  | RC0603FR-0710KL
 |  | R32 | 12.1k | 1% |  | RC0603FR-0712K1L
 |  | R33 | 30.1k | 1% |  | RC0603FR-0730K1L
 |  | R34 | 60.4k | 1% |  | RC0603FR-0760k4L
 |  | R35 | 200 | 1% |  | RC0603FR-07200RL
 |  | R36 | 1.1k | 1% |  | RC0603FR-071K1L
 |  | R37 | 2.49k | 1% |  | RC0603FR-072K49L
 |  | R38 | 10k | 1% |  | RC0603FR-0710KL
 |  | R39 | 1500 | 1% |  | RC0603FR-071K5L
 |  | R40 | 1500 | 1% |  | RC0603FR-071K5L
 |  | R41 | 10k | 5% |  | RC0603FR-0710KL
 |  | R42 | 499 | 1% |  | RC0603FR-07499RL
 |  | R43 | 499 | 1% |  | RC0603FR-07499RL
 |  | R44 | 33 | 1% |  | RC0603FR-0733RL
 |  | R45 | 33 | 1% |  | RC0603FR-0733RL
 |  | R46 | 3.01k | 1% |  | RC0603FR-073k01L
 |  | R47 | 33.2k | 1% |  | RC0603FR-0733K2L
 |  | R48 | 27.4k | 1% |  | RC0603FR-0727K4L
 |  | R49 | 3.01k | 1% |  | RC0603FR-073k01L
 |  | R50 | 10k | 1% |  | RC0603FR-0710KL
 |  | R51 | DNI | 1% |  | RC0603FR-070RL
 |  | R52 | 4.7M | 0.1 |  | RG3216P-4704-B-T1
 |  | R53 | 0 | 0.1 |  | RC0603FR-070RL
 |  | R54 | 0 | 0.1 |  | RC0603FR-070RL
 |  | R55 | DNI | 1% |  | RC0603FR-0710KL
 |  | R56 | 10k | 1% |  | RC0603FR-0710KL
 |  | R57 | 33 | 1% |  | RC0603FR-0733RL
 |  | R58 | 120 | 1% |  | RC0603FR-07120RL
 |  | R59 | 4.7M | 0.1 |  | RG3216P-4704-B-T1
 |  | R60 | 4.7M | 0.1 |  | RG3216P-4704-B-T1
 |  | R61 | 470k | 0.1 |  | RC0603FR-07470KL
 |  | R62 | 10k | 0.1 |  | RC0603FR-0710KL
 |  | R63 | 30k | 1% |  | RC0603FR-0730KL
 |  | R64 | 3k | 1% |  | RC0603FR-073KL
 |  | R65 | DNI | 5% |  | RC0603FR-0710KL
 |  | R66 | 1 | 1% |  | RC0603FR-071RL
 |  | R67 | DNI | 1% |  | RC0603FR-070RL
 |  | R68 | 0 | 5% |  | RC0603FR-070RL
 |  | R69 | DNI | 1%
 |  | R70 | DNI | 1%
 |  | R71 | 0 | 1% |  | RC0603FR-070RL
 |  | R72 | 0 | 5% |  | RC0603FR-070RL
 |  | R73 | 0 | 1% |  | RC0603FR-070RL
 |  | R74 | 0 | 1% |  | RC0603FR-070RL
 |  | U1 | OPA828 |  |  | OPA828ID | OPA1641AIDR | OPA1655DR | AD820BRZ | ADA4625-1ARDZ-R7
 |  | U2 | ADG1208 |  |  | MUX36S08IPWR | ADG1208YRUZ-REEL7
 |  | U3 | G6L-1F-TR-DC5 |  |  | G6L-1F-TR-DC5 | G6L-1F-DC4.5
 |  | U4 | G6L-1F-TR-DC5 |  |  | G6L-1F-TR-DC5 | G6L-1F-DC4.5
 |  | U5 | G6L-1F-TR-DC5 |  |  | G6L-1F-TR-DC5 | G6L-1F-DC4.5
 |  | U6 | 24AA025UID |  |  | 24AA025UIDT-I/SN | 24AA025E64-I/SN
 |  | U7 | MIC5270 |  |  | MIC5270-4.1YM5-TR | MIC5270YM5-TR
 |  | U8 | OPA2156xD |  |  | OPA2156IDR | OPA1656ID | OPA1688ID
 |  | U9 | LP2981A-33DBVT |  |  | LP2981A-33DBVT | LP2985-33DBVR | LP2985-33DBVRG4 | TPS7A2433DBVR
 |  | U10 | LP2951_SOIC |  |  | LP2951-30DR | LP2951-03YM-TR | LP2951ACDR2G
 |  | U11 | OPA991S |  |  | OPA991SIDBVR | OPA990SIDBVR
 |  | U12 | TCA9555DBR |  |  | TCA9555DBR | TCA9555DBT
 |  | U13 | TCA9555DBR |  |  | TCA9555DBR | TCA9555DBT
 |  | U14 | DG412xUE |  |  | DG412CUE+ | TMUX6111PWR | TMUX6112PWR | TMUX6113PWR
 |  | U15 | OPA828 |  |  | OPA828ID | OPA1641AIDR | OPA1655DR | ADA4625-1ARDZ-R7 | AD820BRZ
 |  | U16 | TMUX6111PWR |  |  | TMUX6111PWR | TMUX6112PWR | TMUX6113PWR
 |  | U17 | DG412xUE |  |  | DG412CUE+ | TMUX6111PWR | TMUX6112PWR
 |  | U18 | AD8421ARZ |  |  | AD8421ARZ | INA849DR | AD8429ARZ
 |  | U19 | DNI |  |  | TMUX6136PWR
 |  | U20 | TMUX6111PWR |  |  | TMUX6111PWR | TMUX6112PWR | DG412CUE+
 |  | U21 | TMUX6111PWR |  |  | TMUX6111PWR | TMUX6112PWR | DG412CUE+
 |  | U22 | DNI |  |  | TMUX6136PWR
 |  | U23 | OPA188xxDBV |  |  | OPA188AIDBVR | OPA180IDBVT | OPA202IDBVT
 |  | U24 | LMP8350MA_NOPB |  |  | LMP8350MAX/NOPB | LMP8350MA/NOPB | AD8138AARZ-R7
 |  | U25 | OPA2156xD |  |  | OPA2156IDR | OPA1656ID | OPA1688ID
Collated Components:
Item | Qty | Reference(s) | Value | Tolerance | voltage | Manf# | Alternate Manf# | Alternate2 Manf# | Alternate3 Manf# | Alternate4 Manf# | Alternate Manf# (footprint diff)
1 | 6 | C1, C27, C28, C37, C48, C49 | DNI | 20% | 25V | CC0603FRNPO0BN680
2 | 1 | C2 | 1u | 10% | 25V | 06033C105KAT4A
3 | 1 | C3 | 10u | 10% | 16V | CL21A106KOQNNNE
4 | 23 | C4, C7, C8, C13, C14, C20, C21, C22, C29, C30, C31, C32, C34, C35, C36, C38, C39, C40, C41, C42, C43, C44, C47 | 0.1u | 10% | 25V | CL10B104KA8NNWC
5 | 1 | C5 | 4.7u | 20% | 25V | CL10A475KP8NNNC
6 | 1 | C6 | 4.7n | 5% | 50V | CC0603JRX7R9BB472
7 | 1 | C9 | 47pF | 5% | 50V | CC0603JRNPO9BN470
8 | 1 | C10 | 200pF |  | 50V | CC0603JRNPO9BN221
9 | 1 | C11 | 1nF | 5% | 50V | CC0603JRNPO9BN102
10 | 1 | C12 | 4.7nF | 5% | 50V | CC0603JRNPO9BN332 | CL10C332JB8NNNC
11 | 2 | C15, C16 | 4.7u | 10% | 25V | CL31B475KAHNFNE
12 | 3 | C17, C18, C19 | 0.01u | 20% | 25V | CC0603MRX7R8BB103
13 | 1 | C23 | 68p | 20% | 25V | CC0603FRNPO0BN680
14 | 1 | C24 | 20p | 20% | 25V | CC0603JRNPO9BN200
15 | 1 | C25 | 8p | 20% | 25V | 06031A8R0CAT2A
16 | 1 | C26 | 4p | 20% | 25V | CC0603CRNPO9BN4R0
17 | 1 | C33 | 5p | 5% | 50V | CC0603JRX7R9BB472
18 | 2 | C45, C46 | 10u | 10% | 25V | CL31B106KAHNFNE
19 | 5 | D1, D2, D3, D4, D5 | 1N4007 |  |  | 1N4007FLTR
20 | 1 | FB1 | Ferrite_Bead |  |  | BLM31PG500SN1L
21 | 4 | H1, H3, H5, H7 | DNI
22 | 1 | IC1 | DAC101C081CIMK_NOPB |  |  | DAC101C081CIMK/NOPB | DAC121C081CIMK/NOPB
23 | 3 | J1, J2, J3 | 105-1103-001 |  |  | 105-1103-001
24 | 1 | J4 | HDMI_A |  |  | 10029449-111RLF
25 | 1 | J5 | Conn_01x04 |  |  | PR20204VBNN
26 | 2 | K1, K2 | 1462042-7 |  |  | 1462042-7 |  |  |  |  | 1462042-8
27 | 3 | Q1, Q3, Q4 | MBT3904DW1T1G |  |  | MBT3904DW1T1G
28 | 1 | Q2 | BC856 |  |  | BC856B-7-F
29 | 12 | R1, R20, R23, R26, R27, R53, R54, R68, R71, R72, R73, R74 | 0 | 5% |  | RC0603FR-070RL
30 | 13 | R2, R9, R10, R11, R12, R13, R22, R31, R38, R41, R50, R56, R62 | 10k | 5% |  | RC0603FR-0710KL
31 | 2 | R3, R47 | 33.2k | 5% |  | RC0603FR-0733K2L
32 | 1 | R4 | 100k | 5% |  | RC0603FR-07100KL
33 | 1 | R5 | 332k | 5% |  | RC0603FR-07332KL
34 | 1 | R6 | 1M | 5% |  | RC0603FR-071ML
35 | 1 | R7 | 3.32M | 5% |  | RC0603FR-073M32L
36 | 1 | R8 | 10M | 5% |  | RC0603FR-0710ML
37 | 2 | R14, R17 | 240 | 1% |  | RC0603FR-07240RL
38 | 1 | R15 | 487 | 1% |  | RC0603FR-07487RL
39 | 1 | R16 | 1.13k | 1% |  | RC0603FR-071K13L
40 | 5 | R18, R24, R44, R45, R57 | 33 | 1% |  | RC0603FR-0733RL
41 | 3 | R19, R25, R30 | 20k | 5% |  | RC0603FR-0720KL
42 | 1 | R21 | 2k | 1% |  | RC0603FR-0773K2L
43 | 4 | R28, R52, R59, R60 | 4.7M | 0.1 |  | RG3216P-4704-B-T1
44 | 7 | R29, R51, R55, R65, R67, R69, R70 | DNI | 1% |  | RC0603FR-0773K2L
45 | 1 | R32 | 12.1k | 1% |  | RC0603FR-0712K1L
46 | 1 | R33 | 30.1k | 1% |  | RC0603FR-0730K1L
47 | 1 | R34 | 60.4k | 1% |  | RC0603FR-0760k4L
48 | 1 | R35 | 200 | 1% |  | RC0603FR-07200RL
49 | 1 | R36 | 1.1k | 1% |  | RC0603FR-071K1L
50 | 1 | R37 | 2.49k | 1% |  | RC0603FR-072K49L
51 | 2 | R39, R40 | 1500 | 1% |  | RC0603FR-071K5L
52 | 2 | R42, R43 | 499 | 1% |  | RC0603FR-07499RL
53 | 2 | R46, R49 | 3.01k | 1% |  | RC0603FR-073k01L
54 | 1 | R48 | 27.4k | 1% |  | RC0603FR-0727K4L
55 | 1 | R58 | 120 | 1% |  | RC0603FR-07120RL
56 | 1 | R61 | 470k | 0.1 |  | RC0603FR-07470KL
57 | 1 | R63 | 30k | 1% |  | RC0603FR-0730KL
58 | 1 | R64 | 3k | 1% |  | RC0603FR-073KL
59 | 1 | R66 | 1 | 1% |  | RC0603FR-071RL
60 | 2 | U1, U15 | OPA828 |  |  | OPA828ID | OPA1641AIDR | OPA1655DR | AD820BRZ | ADA4625-1ARDZ-R7
61 | 1 | U2 | ADG1208 |  |  | MUX36S08IPWR | ADG1208YRUZ-REEL7
62 | 1 | U3 | G6L-1F-TR-DC5 |  |  | G6L-1F-TR-DC5 | G6L-1F-DC4.5
63 | 2 | U4, U5 | G6L-1F-TR-DC5 |  |  | G6L-1F-TR-DC5 | G6L-1F-DC4.5
64 | 1 | U6 | 24AA025UID |  |  | 24AA025UIDT-I/SN | 24AA025E64-I/SN
65 | 1 | U7 | MIC5270 |  |  | MIC5270-4.1YM5-TR | MIC5270YM5-TR
66 | 2 | U8, U25 | OPA2156xD |  |  | OPA2156IDR | OPA1656ID | OPA1688ID
67 | 1 | U9 | LP2981A-33DBVT |  |  | LP2981A-33DBVT | LP2985-33DBVR | LP2985-33DBVRG4 | TPS7A2433DBVR
68 | 1 | U10 | LP2951_SOIC |  |  | LP2951-30DR | LP2951-03YM-TR | LP2951ACDR2G
69 | 1 | U11 | OPA991S |  |  | OPA991SIDBVR | OPA990SIDBVR
70 | 2 | U12, U13 | TCA9555DBR |  |  | TCA9555DBR | TCA9555DBT
71 | 2 | U14, U17 | DG412xUE |  |  | DG412CUE+ | TMUX6111PWR | TMUX6112PWR | TMUX6113PWR
72 | 3 | U16, U20, U21 | TMUX6111PWR |  |  | TMUX6111PWR | TMUX6112PWR | TMUX6113PWR
73 | 1 | U18 | AD8421ARZ |  |  | AD8421ARZ | INA849DR | AD8429ARZ
74 | 2 | U19, U22 | DNI |  |  | TMUX6136PWR
75 | 1 | U23 | OPA188xxDBV |  |  | OPA188AIDBVR | OPA180IDBVT | OPA202IDBVT
76 | 1 | U24 | LMP8350MA_NOPB |  |  | LMP8350MAX/NOPB | LMP8350MA/NOPB | AD8138AARZ-R7

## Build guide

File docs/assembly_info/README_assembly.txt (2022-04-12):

README for PCB fabrication and turnkey assembly
contact: Lucas Koerner, koerner.lucas@stthomas.edu 
2022/04/11
cell 408-386-7832
office 651-962-7742
Board name: bath_clamp
-----------------------------

Boards to be standard thickness 1.6 mm and have. 
RoHS is not required but is OK if less expensive. 

170 components 

The part position file is provided with .pos extension; top and bottom are in the same file.
Fab files are provided as PDF with 1:1 scaling. top_fabfile.pdf, bottom_fabfile.pdf
A .zip file of gerbers is provided which includes the drill files.
The BOM is provided as 'bath_clamp_bom.xlsx'. 
Please use the 'Manf#' column as the priority column to determine the part to purchase. Some parts that are low in stock have been provided an 'Alternative Manf#' column.  
 
Equivalent parts may be used for resistors and capacitors if voltage rating and tolerances are maintained. 
Please check with me when alternative ICs are used.

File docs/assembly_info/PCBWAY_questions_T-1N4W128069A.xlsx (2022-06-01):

T-1N4W128069A-BOM
7 | CC0603JRNPO9BN221 | C_0603_1608Metric | 200pF『 』『 』50V | C10 | 1 | 16 |  | The component is 220PF instead of 200PF, should we solder as it is? Yes, please solder as it is. (C10)
9 | CC0603JRNPO9BN332 | C_0603_1608Metric | 4.7nF『 』0.05『 』50V | C12 | 1 | 16 |  | The component is 3.3NF instead of 4.7nF, should we solder as it is? Yes, please solder as it is. (C12)
20 | DAC101C081CIMK/NOPB | Package_TO_SOT_SMD:TSOT-23-6_HandSoldering | DAC101C081CIMK_NOPB『 』『 』 | IC1 | 1 | 16 | Brand : TI 2017. | The component is smaller than the pads on the board, it can be soldered, should we solder as it is？ Yes, please solder as it is. (IC1)
40 | RC0603FR-0773K2L | R_0603_1608Metric | 2k『 』0.01『 』 | R21 | 1 | 16 |  | The component is 73.2k instead of 2k, should we solder as it is? No. If you can, please replace with a resistor as close as possible to 2.2k (from 1.5 k - 2.5 k). If this is not possible DNI (do not install). (R21)

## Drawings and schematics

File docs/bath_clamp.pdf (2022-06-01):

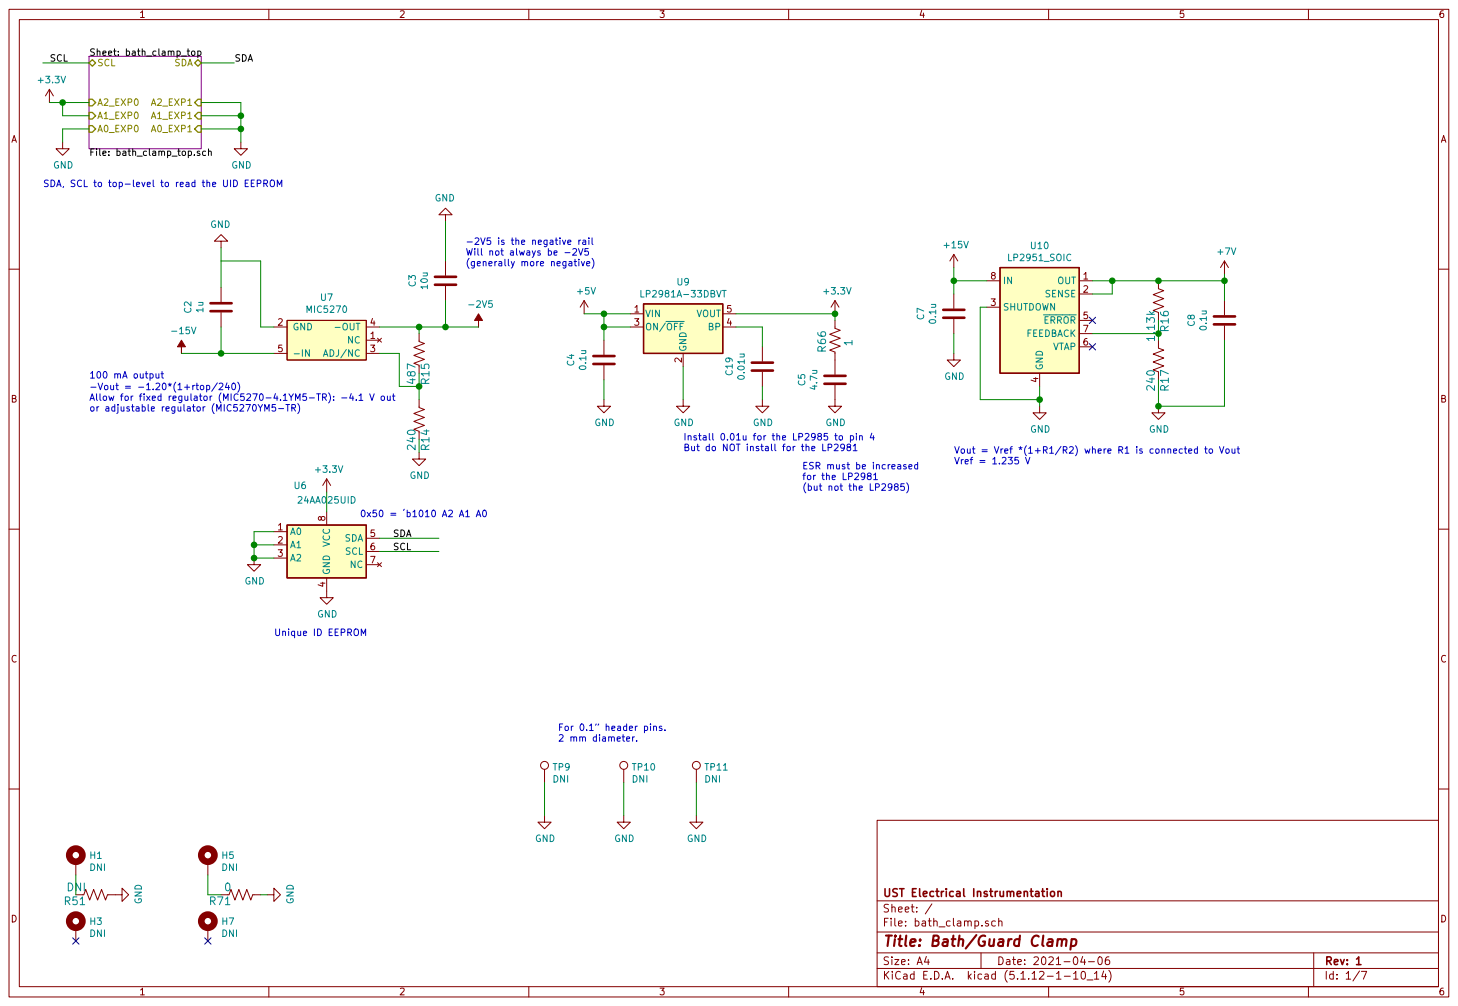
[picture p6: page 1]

SDA, SCL to top-level to read the UID EEPROM

-2V5 is the negative rail
Will not always be -2V5
(generally more negative)

2 ON/OFF 3 BP 4 VOUT 5 U9

100 mA output
-Vout = -1.20*(1+rtop/240)
Allow for fixed regulator (MIC5270-4.1YM5-TR): -4.1 V out
or adjustable regulator (MIC5270YM5-TR)

Install 0.01u for the LP2985 to pin 4 But do NOT install for the LP2981

Vout = Vref *(1+R1/R2) where R1 is connected to Vout Vref = 1.235 V

ESR must be increased
for the LP2981
(but not the LP2985)

4 SDA 5 SCL 6 NC 7 VCC

For 0.1 header pins. 2 mm diameter.
TP10 DNI GND

File: bath_clamp.sch Sheet: / UST Electrical Instrumentation

Id: 1/7 Title: Bath/Guard Clamp

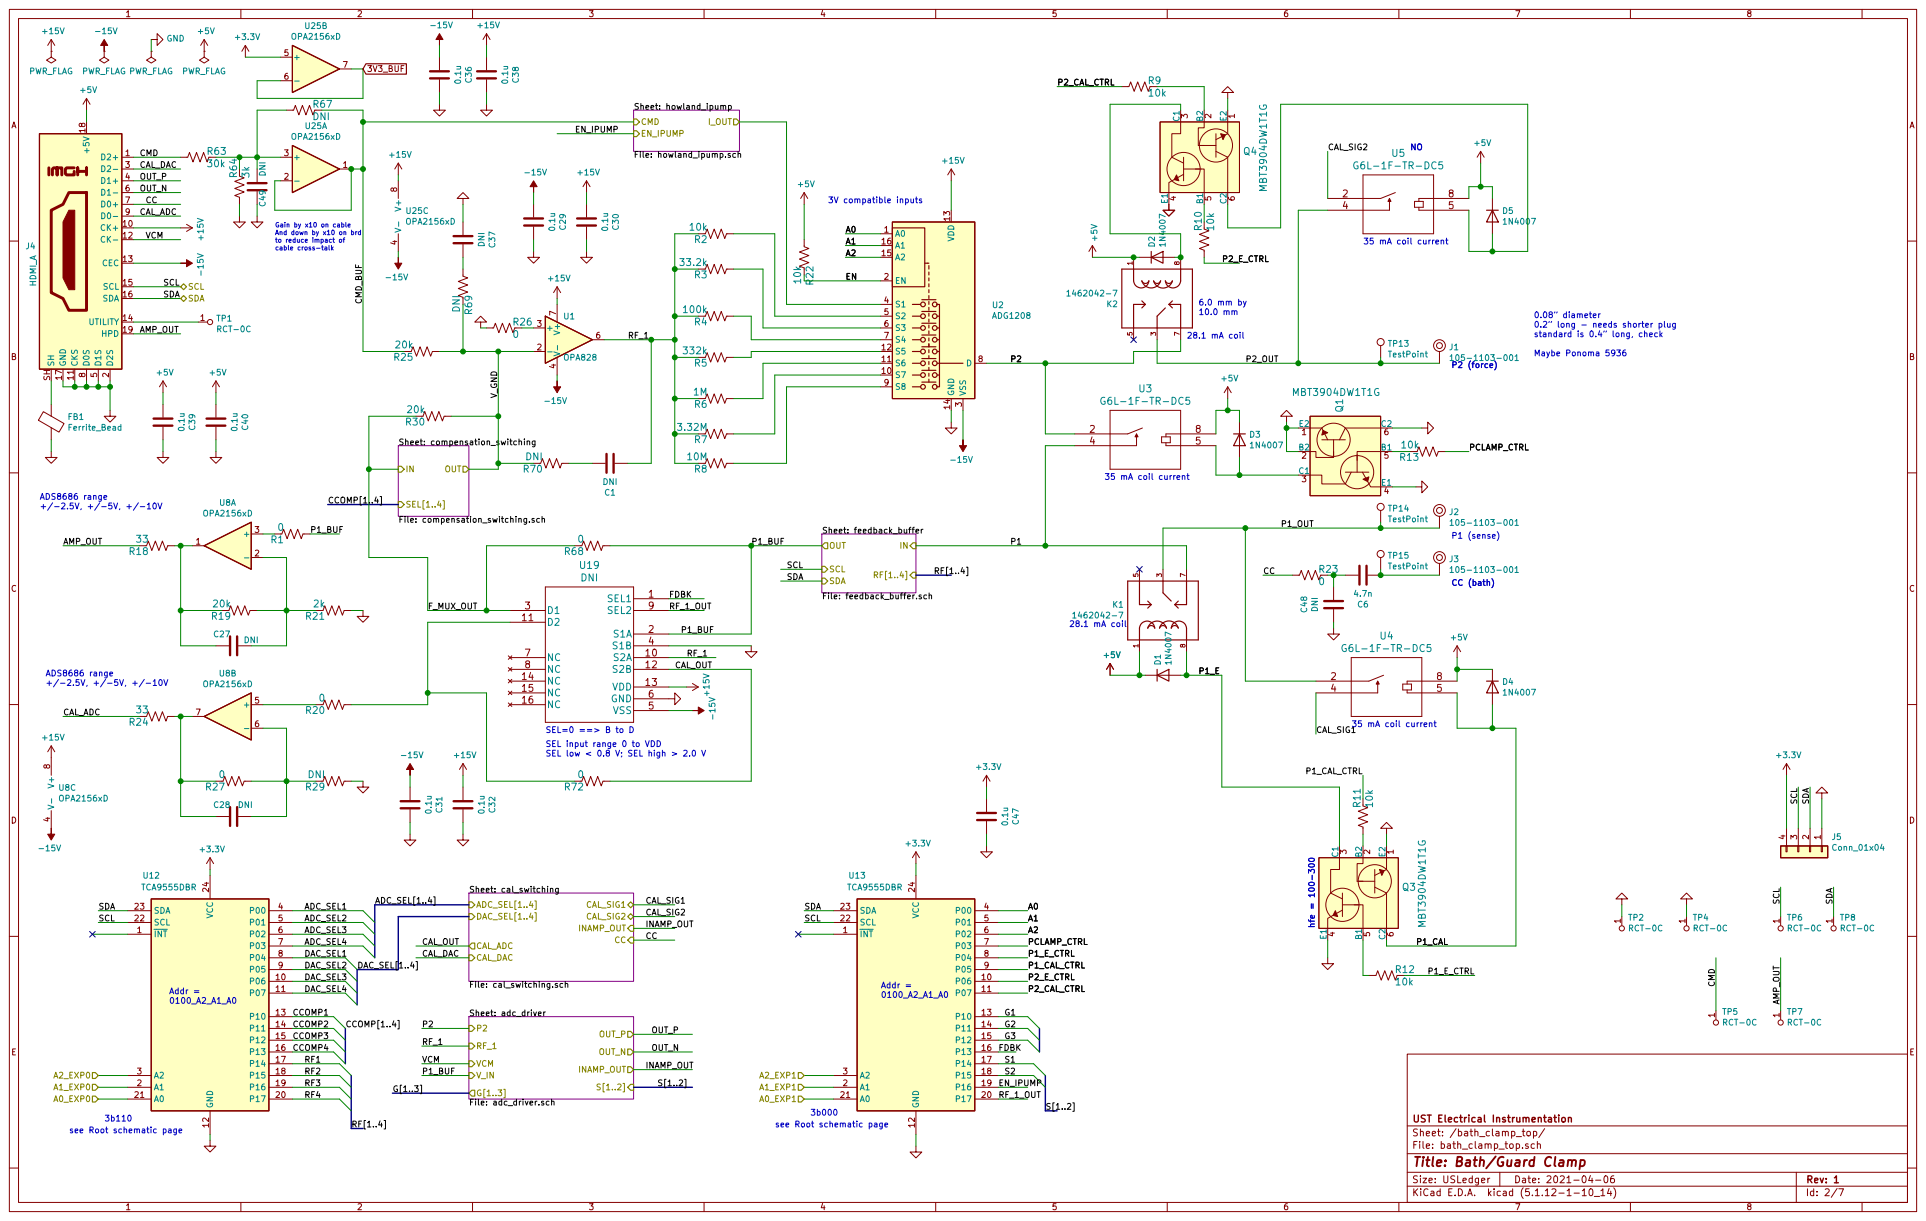
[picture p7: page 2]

Gain by x10 on cable And down by x10 on brd

0.08 diameter 0.2 long - needs shorter plug

P2 (force) 28.1 mA coil ADS8686 range +/-2.5V, +/-5V, +/-10V

standard is 0.4 long, check

P1 (sense) 35 mA coil current 28.1 mA coil

35 mA coil current hfe = 100-300

SEL low < 0.8 V; SEL high > 2.0 V

Sheet: /bath_clamp_top/ UST Electrical Instrumentation

File: bath_clamp_top.sch
Id: 2/7 Title: Bath/Guard Clamp

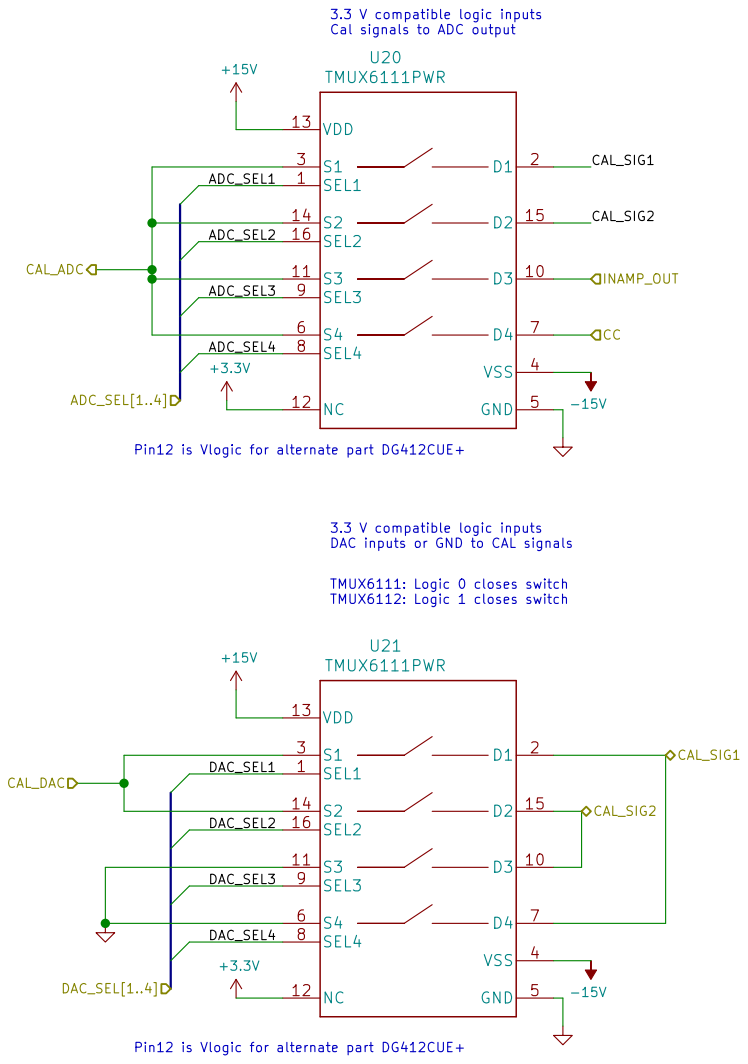
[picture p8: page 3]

3.3 V compatible logic inputs
Cal signals to ADC output

Pin12 is Vlogic for alternate part DG412CUE+

DAC inputs or GND to CAL signals

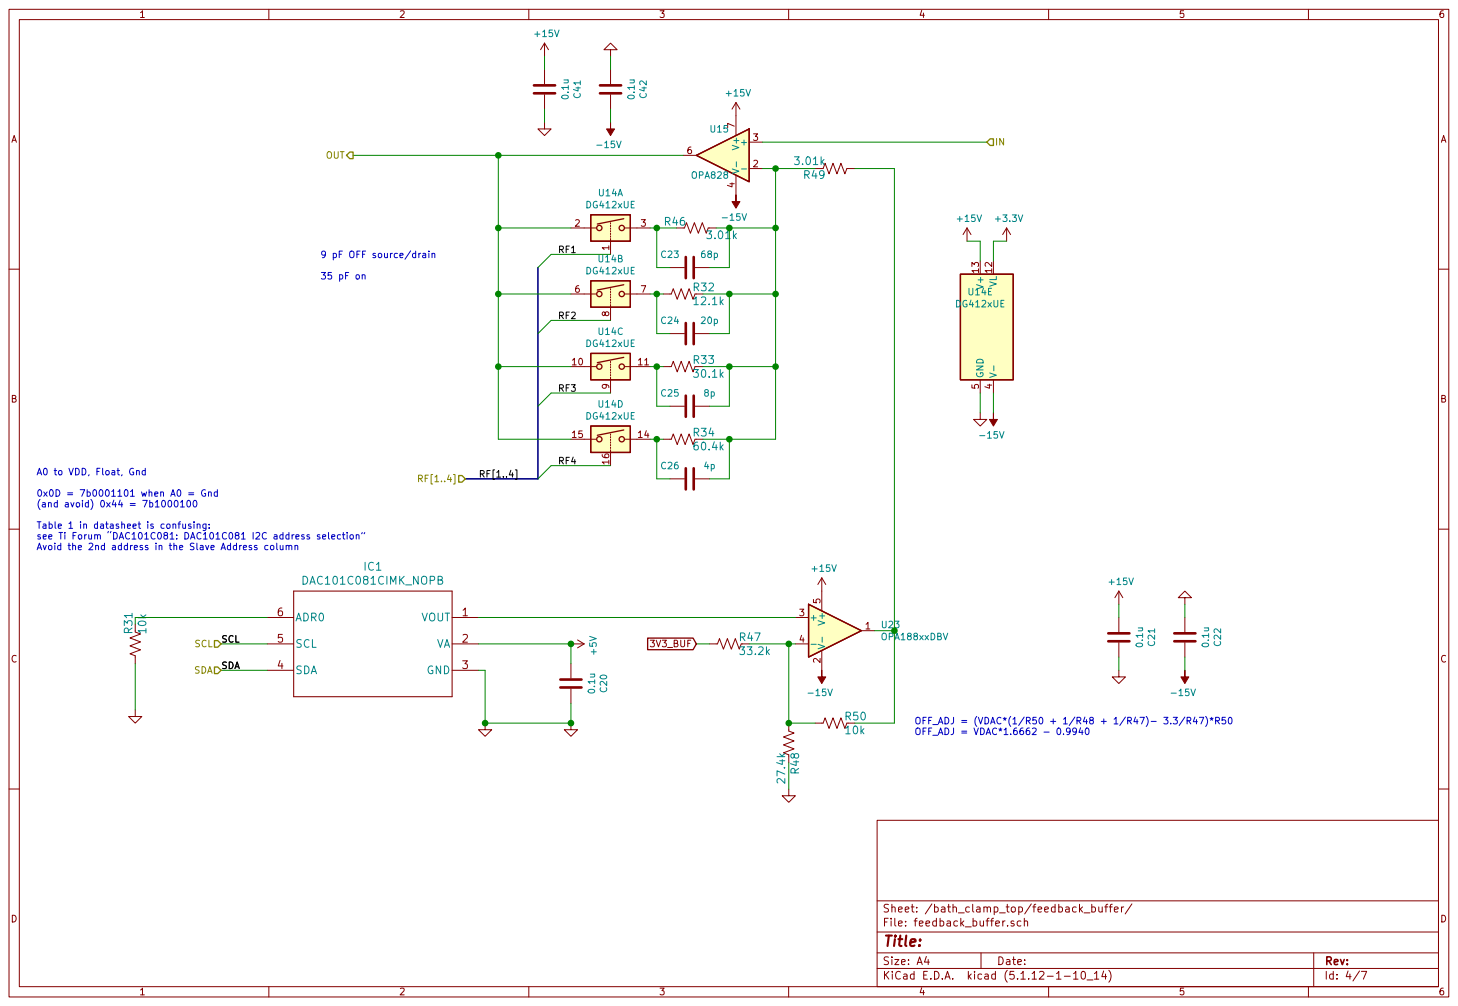
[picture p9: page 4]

9 pF OFF source/drain

Table 1 in datasheet is confusing: see Ti Forum DAC101C081: DAC101C081 I2C address selection Avoid the 2nd address in the Slave Address column

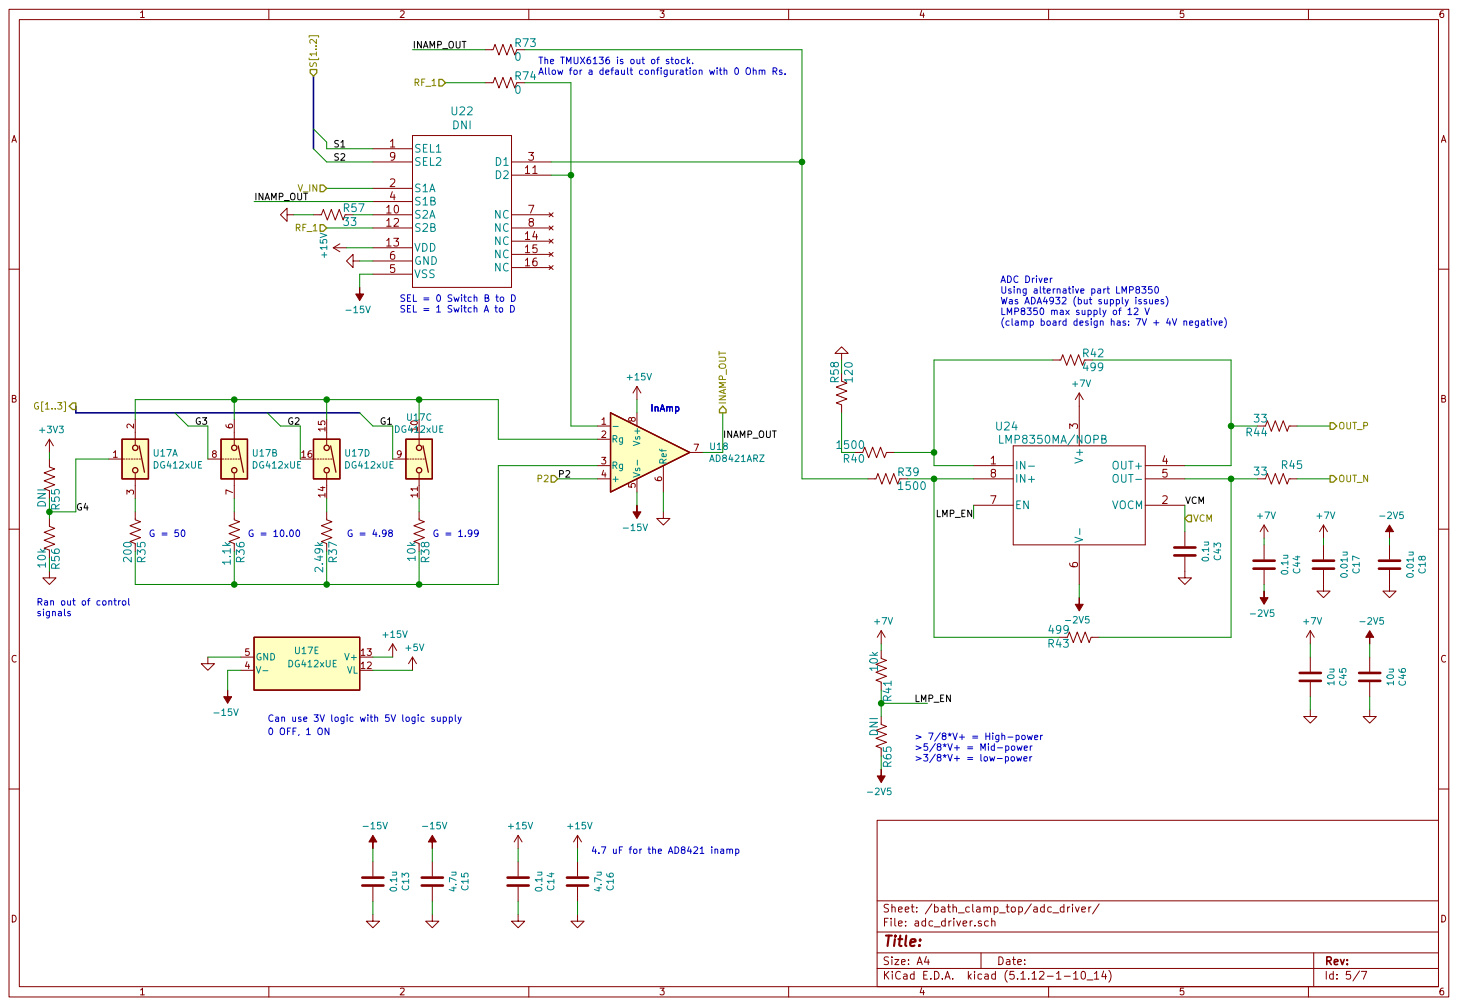
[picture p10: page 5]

Was ADA4932 (but supply issues)
LMP8350 max supply of 12 V
(clamp board design has: 7V + 4V negative)

4.7 uF for the AD8421 inamp Ran out of control signals

Can use 3V logic with 5V logic supply

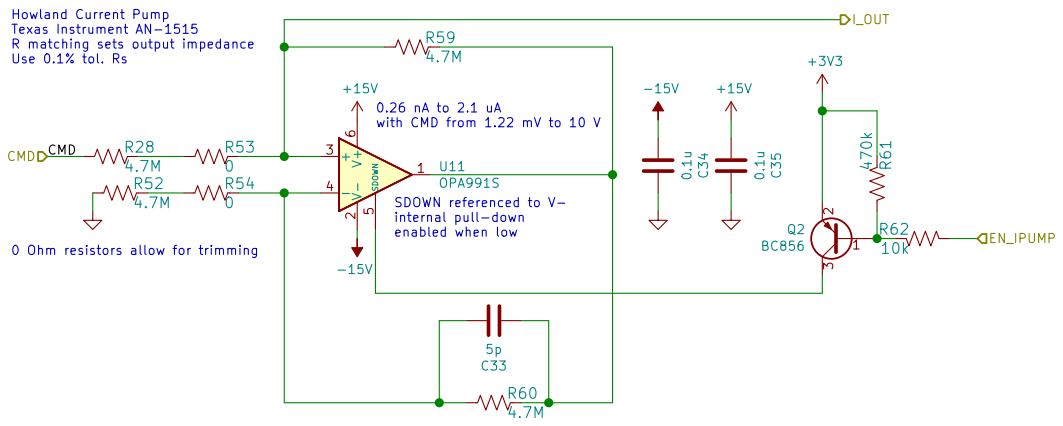
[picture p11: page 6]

0 Ohm resistors allow for trimming

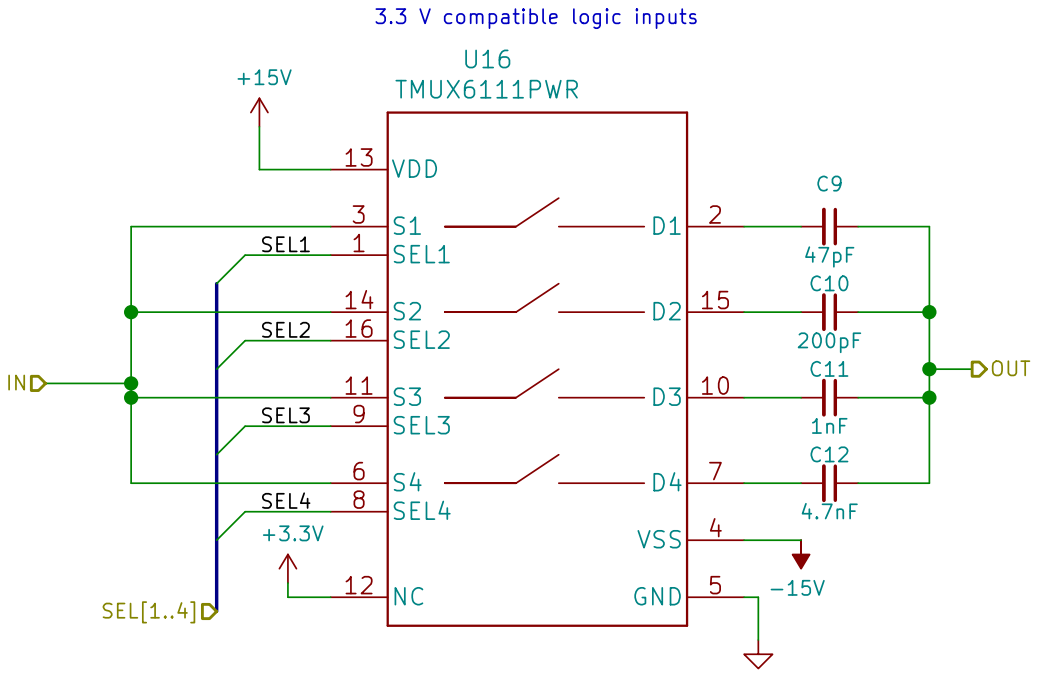
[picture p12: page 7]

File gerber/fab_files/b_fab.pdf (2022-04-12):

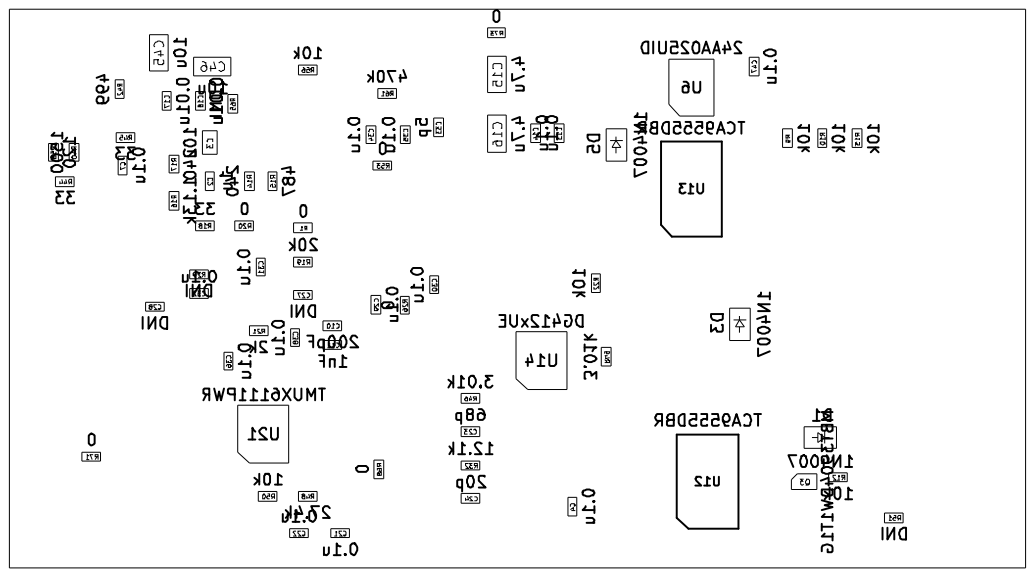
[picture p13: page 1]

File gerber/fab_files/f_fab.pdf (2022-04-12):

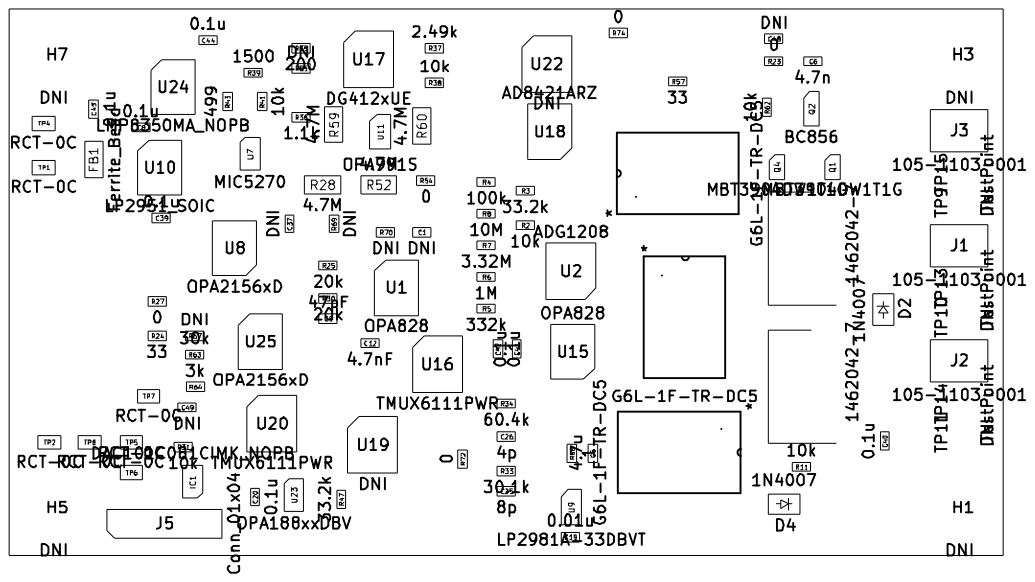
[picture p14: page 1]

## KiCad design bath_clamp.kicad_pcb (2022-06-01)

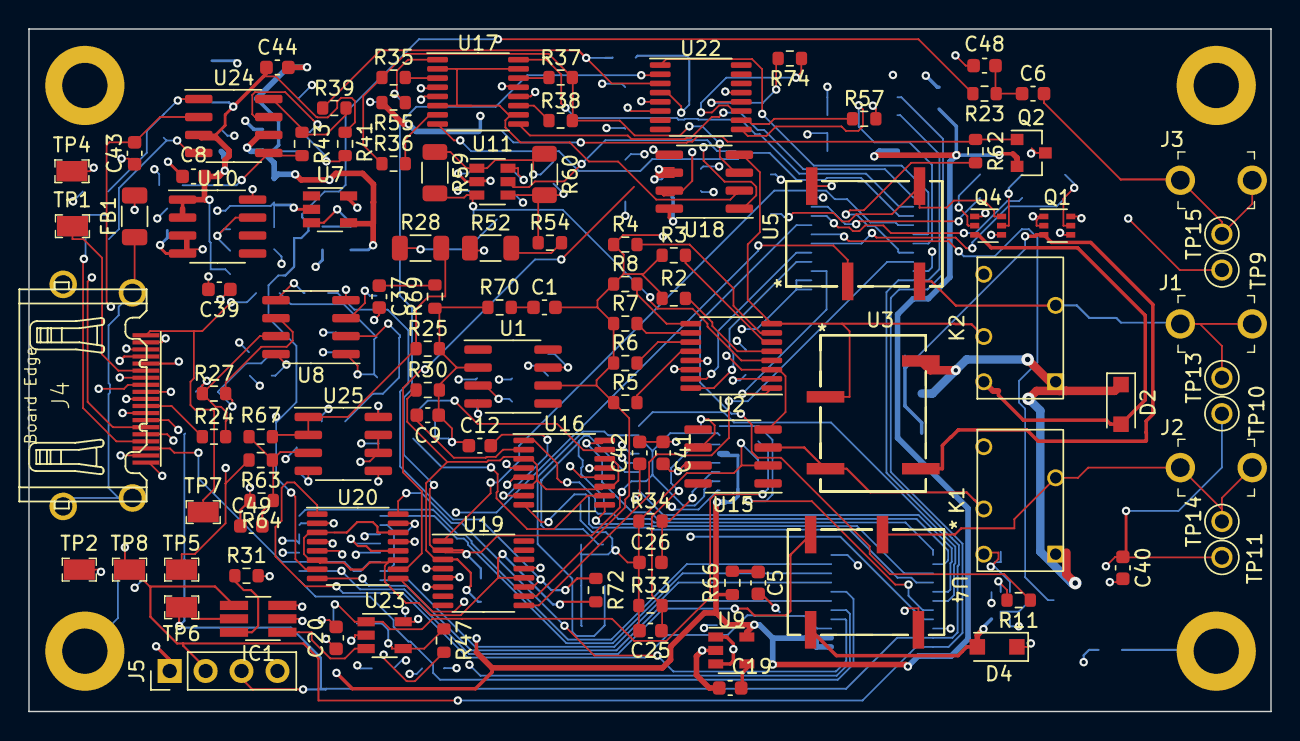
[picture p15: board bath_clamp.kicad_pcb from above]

Board: 6 copper layers, 87.8 x 48.3 mm, 183 parts (0 on the bottom side), 138 nets.

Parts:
C1, C27, C28, C37, C48, C49: DNI; C_0603_1608Metric
C2: 1u; C_0603_1608Metric
C3: 10u; C_0805_2012Metric
C4, C7, C8, C13, C14, C20, C21, C22, C29, C30, C31, C32, C34, C35, C36, C38, C39, C40, C41, C42, C43, C44, C47: 0.1u; C_0603_1608Metric
C5: 4.7u; C_0603_1608Metric
C6: 4.7n; C_0603_1608Metric
C9: 47pF; C_0603_1608Metric
C10: 200pF; C_0603_1608Metric
C11: 1nF; C_0603_1608Metric
C12: 4.7nF; C_0603_1608Metric
C15, C16: 4.7u; C_1206_3216Metric
C17, C18, C19: 0.01u; C_0603_1608Metric
C23: 68p; C_0603_1608Metric
C24: 20p; C_0603_1608Metric
C25: 8p; C_0603_1608Metric
C26: 4p; C_0603_1608Metric
C33: 5p; C_0603_1608Metric
C45, C46: 10u; C_1206_3216Metric
D1, D2, D3, D4, D5: 1N4007; D_SOD-123F
FB1: Ferrite_Bead; C_1206_3216Metric
H1, H3, H5, H7: DNI; MountingHole_3.2mm_M3_DIN965_Pad
IC1: DAC101C081CIMK_NOPB; TSOT-23-6_HandSoldering
J1, J2, J3: 105-1103-001; Test_Jack_Horiz
J4: HDMI_A; CONN_10029449-111RLF_HDMI_A
J5: Conn_01x04; PinHeader_1x04_P2.54mm_Vertical
K1, K2: 1462042-7; Relay_SPDT_TE_1462042-7
Q1, Q3, Q4: MBT3904DW1T1G; SOT-363_SC-70-6
Q2: BC856; SOT-23
R1, R20, R23, R26, R27, R53, R54, R68, R71, R72, R73, R74: 0; R_0603_1608Metric
R2, R9, R10, R11, R12, R13, R22, R31, R38, R41, R50, R56, R62: 10k; R_0603_1608Metric
R3, R47: 33.2k; R_0603_1608Metric
R4: 100k; R_0603_1608Metric
R5: 332k; R_0603_1608Metric
R6: 1M; R_0603_1608Metric
R7: 3.32M; R_0603_1608Metric
R8: 10M; R_0603_1608Metric
R14, R17: 240; R_0603_1608Metric
R15: 487; R_0603_1608Metric
R16: 1.13k; R_0603_1608Metric
R18, R24, R44, R45, R57: 33; R_0603_1608Metric
R19, R25, R30: 20k; R_0603_1608Metric
R21: 2k; R_0603_1608Metric
R28, R52, R59, R60: 4.7M; R_1206_3216Metric
R29, R51, R55, R65, R67, R69, R70: DNI; R_0603_1608Metric
R32: 12.1k; R_0603_1608Metric
R33: 30.1k; R_0603_1608Metric
R34: 60.4k; R_0603_1608Metric
R35: 200; R_0603_1608Metric
R36: 1.1k; R_0603_1608Metric
R37: 2.49k; R_0603_1608Metric
R39, R40: 1500; R_0603_1608Metric
R42, R43: 499; R_0603_1608Metric
R46, R49: 3.01k; R_0603_1608Metric
R48: 27.4k; R_0603_1608Metric
R58: 120; R_0603_1608Metric
R61: 470k; R_0603_1608Metric
R63: 30k; R_0603_1608Metric
R64: 3k; R_0603_1608Metric
R66: 1; R_0603_1608Metric
TP1, TP2, TP4, TP5, TP6, TP7, TP8: RCT-0C; PROBE_PAD_0805
TP9, TP10, TP11: DNI; TestPoint_THTPad_D2.0mm_Drill1.0mm
TP13, TP14, TP15: TestPoint; TestPoint_THTPad_D2.0mm_Drill1.0mm
U1, U15: OPA828; SOIC-8_3.9x4.9mm_P1.27mm
U2: ADG1208; TSSOP-16_4.4x5mm_P0.65mm
U3, U4, U5: G6L-1F-TR-DC5
U6: 24AA025UID; SOIC-8_3.9x4.9mm_P1.27mm
U7: MIC5270; TSOT-23-5
U8, U25: OPA2156xD; SOIC-8_3.9x4.9mm_P1.27mm
U9: LP2981A-33DBVT; SOT-23-5
U10: LP2951_SOIC; SOIC-8_3.9x4.9mm_P1.27mm
U11: OPA991S; SOT-23-6
U12, U13: TCA9555DBR; SSOP-24_5.3x8.2mm_P0.65mm
U14, U17: DG412xUE; TSSOP-16_4.4x5mm_P0.65mm
U16, U20, U21: TMUX6111PWR; TSSOP-16_4.4x5mm_P0.65mm
U18: AD8421ARZ; SOIC-8_3.9x4.9mm_P1.27mm
U19, U22: DNI; TSSOP-16_4.4x5mm_P0.65mm
U23: OPA188xxDBV; TSOT-23-5
U24: LMP8350MA_NOPB; SOIC-8_3.9x4.9mm_P1.27mm

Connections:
3V3_BUF: R47.2, U25.6, U25.7
+3V3: C47.2, J5.4, Q2.2, R55.2, R61.1, R66.1, U6.8, U9.5, U12.2, U12.3, U12.24, U13.24, U14.12, U16.12, U20.12, U21.12, U25.5
+5V: C4.1, C20.2, C39.2, C40.2, D1.1, D2.1, D3.1, D4.1, D5.1, IC1.2, J4.18, K1.1, K2.1, R22.2, U3.8, U4.8, U5.8, U9.1, U9.3, U17.12
+7V: C8.1, C17.2, C44.2, C45.2, R16.2, R41.2, U10.1, U10.2, U24.3
+15V: C7.1, C14.2, C16.2, C21.2, C30.2, C32.2, C35.2, C38.2, C41.2, J4.10, U1.7, U2.13, U8.8, U10.8, U11.6, U14.13, U15.7, U16.13, U17.13, U18.8, U19.13, U20.13, U21.13, U22.13, U23.5, U25.8
-2V5: C3.2, C18.2, C44.1, C46.2, R15.2, R65.1, U7.4, U24.6
-15V: C2.2, C13.2, C15.2, C22.1, C29.2, C31.2, C34.2, C36.2, C42.1, J4.13, U1.4, U2.3, U7.5, U8.4, U11.2, U14.4, U15.4, U16.4, U17.4, U18.5, U19.5, U20.4, U21.4, U22.5, U23.2, U25.4
/SCL: IC1.5, J4.15, J5.3, TP6.1, U6.6, U12.22, U13.22
/SDA: IC1.4, J4.16, J5.2, TP8.1, U6.5, U12.23, U13.23
/bath_clamp_top/A0: U2.1, U13.4
/bath_clamp_top/A1: U2.16, U13.5
/bath_clamp_top/A2: U2.15, U13.6
/bath_clamp_top/ADC_SEL1: U12.4, U20.1
/bath_clamp_top/ADC_SEL2: U12.5, U20.16
/bath_clamp_top/ADC_SEL3: U12.6, U20.9
/bath_clamp_top/ADC_SEL4: U12.7, U20.8
/bath_clamp_top/AMP_OUT: J4.19, R18.1, TP7.1
/bath_clamp_top/CAL_ADC: J4.9, R24.1
/bath_clamp_top/CAL_DAC: J4.3, U21.3, U21.14
/bath_clamp_top/CAL_OUT: R72.2, U19.12, U20.3, U20.6, U20.11, U20.14
/bath_clamp_top/CAL_SIG1: U4.4, U20.2, U21.2, U21.7
/bath_clamp_top/CAL_SIG2: U5.2, U20.15, U21.10, U21.15
/bath_clamp_top/CC: J4.7, R23.2, U20.7
/bath_clamp_top/CCOMP1: U12.13, U16.1
/bath_clamp_top/CCOMP2: U12.14, U16.16
/bath_clamp_top/CCOMP3: U12.15, U16.9
/bath_clamp_top/CCOMP4: U12.16, U16.8
/bath_clamp_top/CMD: J4.1, R63.2, TP5.1
/bath_clamp_top/CMD_BUF: R25.1, R28.2, R67.1, U25.1, U25.2
/bath_clamp_top/DAC_SEL1: U12.8, U21.1
/bath_clamp_top/DAC_SEL2: U12.9, U21.16
/bath_clamp_top/DAC_SEL3: U12.10, U21.9
/bath_clamp_top/DAC_SEL4: U12.11, U21.8
/bath_clamp_top/EN: R22.1, U2.2
/bath_clamp_top/EN_IPUMP: R62.2, U13.19
/bath_clamp_top/FDBK: U13.16, U19.1
/bath_clamp_top/F_MUX_OUT: R30.1, R68.1, U16.3, U16.6, U16.11, U16.14, U19.3
/bath_clamp_top/G1: U13.13, U17.9
/bath_clamp_top/G2: U13.14, U17.16
/bath_clamp_top/G3: U13.15, U17.8
/bath_clamp_top/INAMP_OUT: R73.2, U18.7, U20.10, U22.4
/bath_clamp_top/OUT_N: J4.6, R45.2
/bath_clamp_top/OUT_P: J4.4, R44.2
/bath_clamp_top/P1: K1.7, U3.4, U15.3
/bath_clamp_top/P1_BUF: R1.2, R68.2, U14.2, U14.6, U14.10, U14.15, U15.6, U19.2, U22.2
/bath_clamp_top/P1_CAL: D4.2, Q3.6, U4.5
/bath_clamp_top/P1_CAL_CTRL: R11.1, U13.9
/bath_clamp_top/P1_E: D1.2, K1.8, Q3.3
/bath_clamp_top/P1_E_CTRL: R12.1, U13.8
/bath_clamp_top/P1_OUT: J2.1, K1.3, TP14.1, U4.2
/bath_clamp_top/P2: K2.7, U2.8, U3.2, U18.4
/bath_clamp_top/P2_CAL_CTRL: R9.2, U13.11
/bath_clamp_top/P2_E_CTRL: R10.2, U13.10
/bath_clamp_top/P2_OUT: J1.1, K2.3, TP13.1, U5.4
/bath_clamp_top/PCLAMP_CTRL: R13.2, U13.7
/bath_clamp_top/RF1: U12.17, U14.1
/bath_clamp_top/RF2: U12.18, U14.8
/bath_clamp_top/RF3: U12.19, U14.9
/bath_clamp_top/RF4: U12.20, U14.16
/bath_clamp_top/RF_1: C1.2, R2.1, R3.1, R4.1, R5.1, R6.1, R7.1, R8.1, R74.2, U1.6, U19.10, U22.12
/bath_clamp_top/RF_1_OUT: U13.20, U19.9
/bath_clamp_top/S1: U13.17, U22.1
/bath_clamp_top/S2: U13.18, U22.9
/bath_clamp_top/VCM: C43.2, J4.12, U24.2
/bath_clamp_top/V_GND: C9.1, C10.1, C11.1, C12.1, R25.2, R30.2, R69.1, R70.1, U1.2
/bath_clamp_top/adc_driver/G4: R55.1, R56.2, U17.1
/bath_clamp_top/adc_driver/LMP_EN: R41.1, R65.2, U24.7
/bath_clamp_top/howland_ipump/I_OUT: R53.1, R59.2, U2.4, U11.3
GND: C2.1, C3.1, C4.2, C5.2, C7.2, C8.2, C13.1, C14.1, C15.1, C16.1, C17.1, C18.1, C19.2, C20.1, C21.1, C22.2, C29.1, C30.1, C31.1, C32.1, C34.1, C35.1, C36.1, C37.2, C38.1, C39.1, C40.1, C41.1, C42.2, C43.1, C45.1, C46.1, C47.1, C48.2, C49.1, FB1.2, IC1.3, J4.2, J4.5, J4.8, J4.11, J4.17, J5.1, Q1.1, Q1.2, Q1.4, Q1.6, Q3.1, Q3.4, Q4.1, Q4.4, R14.1, R17.1, R21.2, R26.2, R29.2, R31.2, R48.1, R51.2, R52.2, R56.1, R57.2, R58.1, R64.2, R71.2, TP2.1, TP4.1, TP9.1, TP10.1, TP11.1, U2.14, U6.1, U6.2, U6.3, U6.4, U7.2, U9.2, U10.3, U10.4, U12.12, U12.21, U13.2, U13.3, U13.12, U13.21, U14.5, U16.5, U17.5, U18.6, U19.4, U19.6, U20.5, U21.5, U21.6, U21.11, U22.6
unnamed: C1.1, R70.2
unnamed: C5.1, R66.2
unnamed: C6.2, J3.1, TP15.1
unnamed: C9.2, U16.2
unnamed: C10.2, U16.15
unnamed: C11.2, U16.10
unnamed: C12.2, U16.7
unnamed: C19.1, U9.4
unnamed: C23.1, C24.1, C25.1, C26.1, R32.1, R33.1, R34.1, R46.1, R49.1, U15.2
unnamed: C23.2, R46.2, U14.3
unnamed: C24.2, R32.2, U14.7
unnamed: C25.2, R33.2, U14.11
unnamed: C26.2, R34.2, U14.14
unnamed: C27.1, R19.2, R21.1, U8.2
unnamed: C27.2, R18.2, R19.1, U8.1
unnamed: C28.1, R27.2, R29.1, U8.6
unnamed: C28.2, R24.2, R27.1, U8.7
unnamed: C33.1, R54.1, R60.2, U11.4
unnamed: C33.2, R59.1, R60.1, U11.1
unnamed: C37.1, R69.2
unnamed: C6.1, C48.1, R23.1
unnamed: C49.2, R63.1, R64.1, R67.2, U25.3
unnamed: D2.2, K2.8, Q4.3
unnamed: D3.2, Q1.3, U3.5
unnamed: D5.2, Q4.6, U5.5
unnamed: FB1.1, J4.SH
unnamed: H1.1, R51.1
unnamed: H5.1, R71.1
unnamed: IC1.1, U23.3
unnamed: IC1.6, R31.1
unnamed: J4.14, TP1.1
unnamed: Q1.5, R13.1
unnamed: Q2.1, R61.2, R62.1
unnamed: Q2.3, U11.5
unnamed: Q3.2, R11.2
unnamed: Q3.5, R12.2
unnamed: Q4.2, R9.1
unnamed: Q4.5, R10.1
unnamed: R1.1, U8.3
unnamed: R2.2, U2.5
unnamed: R3.2, U2.6
unnamed: R4.2, U2.7
unnamed: R5.2, U2.12
unnamed: R6.2, U2.11
unnamed: R7.2, U2.10
unnamed: R8.2, U2.9
unnamed: R14.2, R15.1, U7.3
unnamed: R16.1, R17.2, U10.7
unnamed: R20.1, U8.5
unnamed: R20.2, R72.1, U19.11
unnamed: R26.1, U1.3
unnamed: R28.1, R53.2
unnamed: R35.1, R36.1, R37.1, R38.1, U18.3
unnamed: R35.2, U17.3
unnamed: R36.2, U17.7
unnamed: R37.2, U17.14
unnamed: R38.2, U17.11
unnamed: R39.1, R43.1, U24.8
unnamed: R39.2, R73.1, U22.3
unnamed: R40.1, R58.2
unnamed: R40.2, R42.2, U24.1
unnamed: R42.1, R44.1, U24.4
unnamed: R43.2, R45.1, U24.5
unnamed: R47.1, R48.2, R50.2, U23.4
unnamed: R49.2, R50.1, U23.1
unnamed: R52.1, R54.2
unnamed: R57.1, U22.10
unnamed: R74.1, U18.1, U22.11
unnamed: U17.2, U17.6, U17.10, U17.15, U18.2

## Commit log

2021-05-07 update gitignore
    [bath_clamp_v1.csv, bom_kifield.csv, my_design_backup.csv]
2021-05-12 offset adjust to feedback buffer
    [adc_driver.sch, bath_clamp_v1.sch, bath_clamp_v1_1.sch, cal_switching.sch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]
2021-05-13 reduced ERC to just 4 warnings
    [adc_driver.sch, bath_clamp_v1.sch, bath_clamp_v1_1.sch, cal_switching.sch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]
2021-05-13 updates to pcb layout
    [adc_driver.sch, bath_clamp_v1.kicad_pcb, bath_clamp_v1.sch, bath_clamp_v1_1.sch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]
2021-05-14 added switching (partially) for current clamp
    [adc_driver.sch, bath_clamp_v1.kicad_pcb, bath_clamp_v1_1.sch]
2021-05-17 before adding Howland for current clamp
    [adc_driver.sch, bath_clamp_v1_1.sch]
2021-05-21 updates to README
    [adc_driver.sch, bath_clamp_v1_1.sch, cal_switching.sch, feedback_buffer.sch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]
2021-05-23 update MUX for adc driver
    [adc_driver.sch, bath_clamp_v1_1.sch]
2021-05-26 added pdf print of schematics
    [adc_driver.sch, bath_clamp_v1_1.sch, my_design_backup.csv]
2021-05-28 made sheet for Howland
    [adc_driver.sch, bath_clamp_v1.kicad_pcb, bath_clamp_v1.sch, bath_clamp_v1_1.sch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]
2021-06-08 removed all references to clamp footprints
    [bath_clamp_v1.kicad_pcb, bath_clamp_v1_1.sch, howland_ipump.sch]
2021-06-08 removed clamp footprints
2021-06-11 layout updates; part positioning
    [adc_driver.sch, bath_clamp_v1.kicad_pcb, bath_clamp_v1.sch, bath_clamp_v1_1.sch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]
2021-06-13 first freerouter trial of routing
    [bath_clamp_v1.kicad_pcb]
2021-06-14 layout updates and 3d models
    [adc_driver.sch, bath_clamp_v1.kicad_pcb, bath_clamp_v1_1.sch, compensation_switching.sch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]
2021-06-17 README updates
    [bath_clamp_v1.kicad_pcb]
2021-06-18 freerouter updates; close to submission
    [bath_clamp_v1.kicad_pcb, bath_clamp_v1_1.sch, bom_kicost.xlsx, bom_kifield.csv]
2021-06-22 updates to schematic plot
    [adc_driver.sch, bath_clamp_v1_1.sch]
2021-07-02 before autoroute
    [bath_clamp_v1.kicad_pcb]
2021-07-08 clamp files at submission to JLCPCB
    [adc_driver.sch, bath_clamp_v1-B_Mask.gbs, bath_clamp_v1-B_Paste.gbp, bath_clamp_v1-B_SilkS.gbo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]
2022-01-19 updating git so that kicad schematic matches pdf doc
    [bath_clamp_v1_bom_assembly.xlsx, bath_clamp_v1_bom_for_home_assembly.xlsx, cal_switching.sch, feedback_buffer.sch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]
2022-03-23 renamed files to remove version number
    [bath_clamp.kicad_pcb, bath_clamp.sch, bath_clamp_top.sch, bath_clamp_v1.csv]
2022-03-23 added many alternate manufacturing part numbers
    [bath_clamp_top.sch, cal_switching.sch, feedback_buffer.sch]
2022-04-02 updates to schematic for alternate part #s
    [adc_driver.sch, bath_clamp.csv, bath_clamp.kicad_pcb, bath_clamp.sch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]
2022-04-05 nearly completed layout re-route
    [adc_driver.sch, bath_clamp.kicad_pcb, bath_clamp.sch, bath_clamp_top.sch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]
2022-04-12 gerbers, BOM and fabrication files sent to PCBway
    [adc_driver.sch, bath_clamp-B_Fab.gbr, bath_clamp-B_Mask.gbs, bath_clamp-B_Paste.gbp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]
2022-06-01 add PDF print of schematic
    [PCBWAY_questions_T-1N4W128069A.xlsx, T-1N4W128069A-16sets-T-1N4W128069A-bath_clamp_bom.xls, adc_driver.kicad_sch, adc_driver.sch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]

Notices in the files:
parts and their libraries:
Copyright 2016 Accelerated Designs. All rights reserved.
